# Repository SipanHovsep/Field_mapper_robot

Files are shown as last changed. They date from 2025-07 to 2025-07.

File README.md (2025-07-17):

# Field Mapper Robot

## Overview
Design of a **modular, cost‑effective robot** for mapping magnetic fields within a defined volume.
<div align="center">
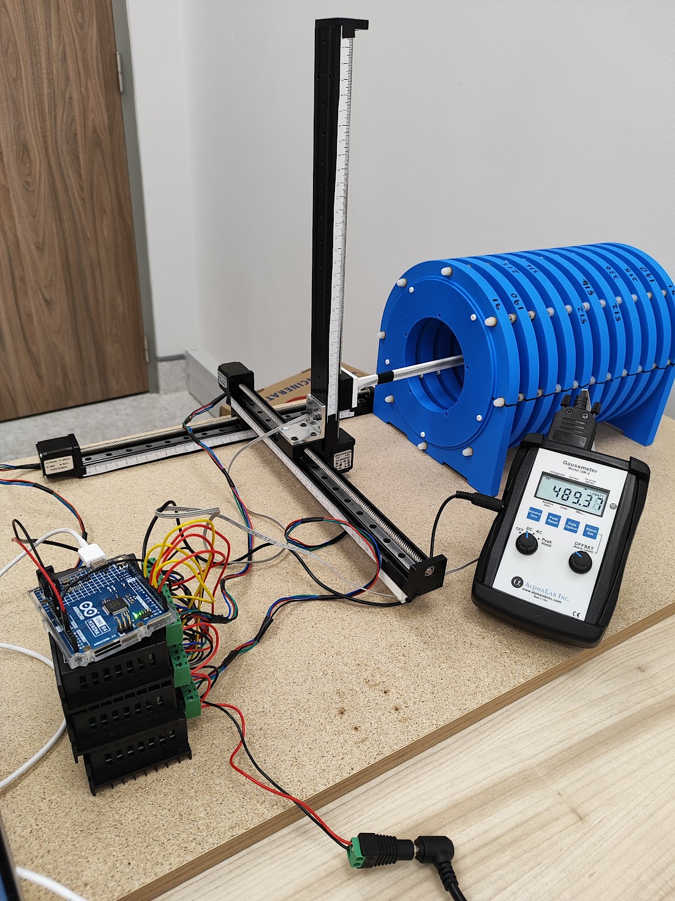
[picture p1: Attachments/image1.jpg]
  
</div>

## Software requirements
* **PyCharm** – Python IDE (Python 3.13) – [Link](https://www.jetbrains.com/pycharm/)
* **Arduino IDE** – Native Arduino software – [Link](https://www.arduino.cc/en/software/)

## Hardware requirements
* **CPU:** 64‑bit dual‑core (modern)  
* **RAM:** ≥ 8 GB (PyCharm needs 2 GB free)  
* **Storage:** ≥ 5 GB free SSD (PyCharm ≈ 3.5 GB + projects)  
* **OS:** Windows 10 64‑bit +, macOS 10.15 +, Ubuntu 20.04 +  
* Basic jumper wires for Arduino  
* M3 screws with nuts  
* USB‑C ↔ USB‑C / USB‑A ↔ USB‑C cable (Arduino Uno R4)  
* Wire cutter/stripper  
* Precision screwdriver set  

---

## Bill of Materials
| Component | Qty | Unit Price (USD) | Link |
|---|:---:|:---:|---|
| Linear stages (Z 300 mm, XY 300 mm – 12 mm pitch) | 1 | 338.54 | [Product](https://www.aliexpress.us/item/3256805348651313.html?spm=a2g0o.order_detail.order_detail_item.3.5fa4f19cjVbIP4&gatewayAdapt=glo2usa) |
| TB6600 stepper driver | 3 | 5.60 | [Product](https://www.aliexpress.us/item/3256805781393725.html?spm=a2g0o.order_detail.order_detail_item.2.1ed6f19cobQnNT&gatewayAdapt=glo2usa) |
| Arduino UNO R4 Minima | 1 | 16.00 | [Product](https://thepihut.com/products/arduino-uno-r4-minima) |
| Gaussmeter GM2 | 1 | 902.00 | [Product](https://www.alphalabinc.com/products/gm2/?srsltid=AfmBOor0p2l-VF9fIRODsZqY854WaDDNnBIFsOJ6kHjN2p6iCgCOzTLX) |
| **Total** |  | **1262.14** |  |

---

## High‑Level Workflow

<div align="center">
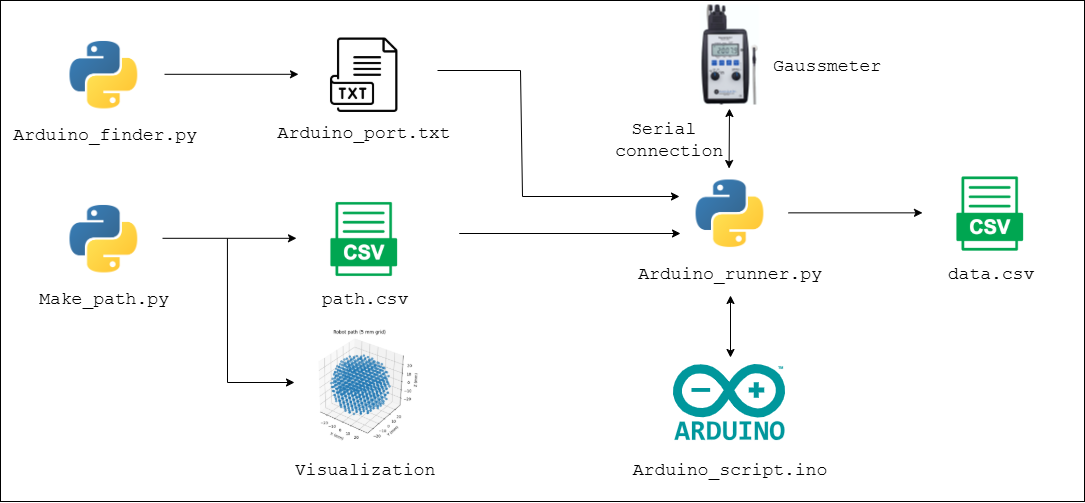
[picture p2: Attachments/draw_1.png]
System flowchart 1
  
</div>
<h3 align="center"><em>Software workflow diagram</em></h3>

<div align="center">
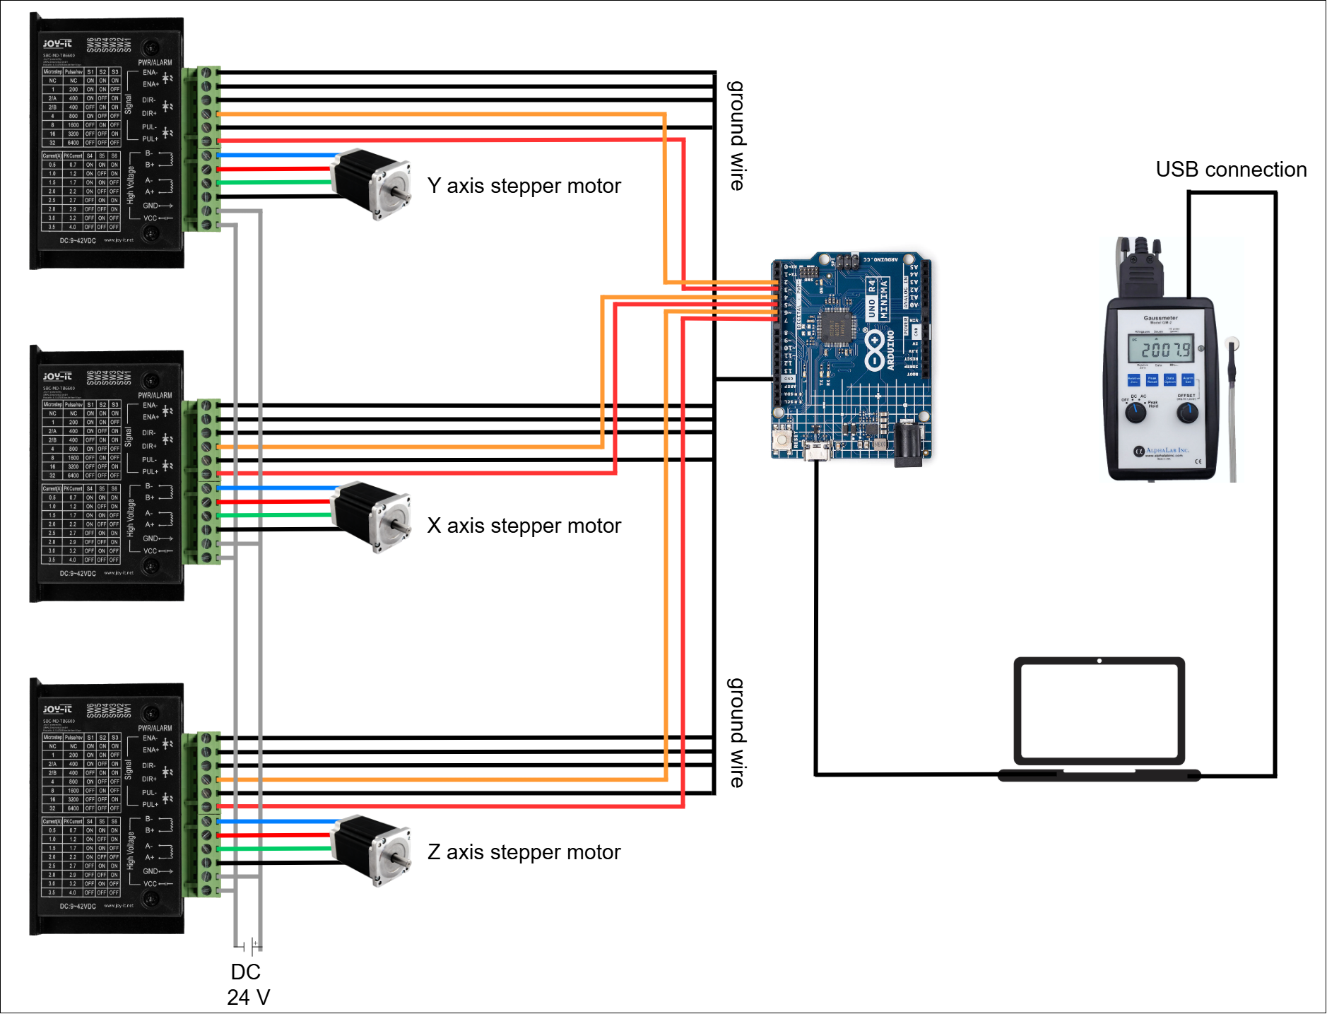
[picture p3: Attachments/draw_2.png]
System flowchart 2
  
</div>
<h3 align="center"><em>Wiring diagram</em></h3>

## Installation and Setup  

1. Clone the repository:  
    ```bash  
    git clone https://github.com/SipanHovsep/Field_mapper_robot
    ```  
2. Install dependencies:  
    ```bash  
    pip install -r requirements.txt  
    ```  
3. Connect the hardware as described in the wiring diagram.
4. Print the files in [3D print files](3D_print_files)
5. Connect and upload [`Arduino_script.ino`](scripts/Arduino_script.ino) to Arduino
6. Run [`Arduino_finder.py`](scripts/Arduino_finder.py)
7. Run [`Path_maker.py`](scripts/Path_maker.py)
8. Run [`Arduino_runner.py`](scripts/Arduino_runner.py)
9. Check out [`Supporting images`](Attachments/Supporting%20images/) for further images
---

## Scripts Overview  

### [`Arduino_finder.py`](scripts/Arduino_finder.py)

- Run once the arduino is connected 
- Finds the connection port name and writes it in Arduino_port.txt file 

### [`Path_maker.py`](scripts/Path_maker.py)

- Generates the path trajectory with discrete points
- Allows user to modify the trajectory and spacing between individual points
- Visualizes the path in 3D with exact sequence the robot would follow, for user to validate
- Writes the x y z coordinates of the path in the right order in "path.CSV" file

### [`Arduino_runner.py`](scripts/Arduino_runner.py)
  
- Allows user to input delay time for sensor read at each desired point and control the speed of robot movement
- Retrieves the coordinates from "path.CSV" file
- Generates text commands to move the robot according to the path
- Sends text commands to arduino at 9600 baud (defined by user) via Arduino port retrieved from Arduino.txt file
- Establishes a serial connection with Gaussmeter through usb port
- Records voltage readings of Gaussmeter per data point and appends to corresponding coordinate
- Generates Data.CSV, containing x y z reading values for each coordinates

### [`Arduino_script.ino`](scripts/Arduino_script.ino)
- Defines Pin map of the arduino
- Listens for simple text commands (X+, X-, Y+, Y-, Z+, Z-,) sent over USB at 9600 baud (Links [`Arduino_runner.py`](scripts/Arduino_runner.py) with Arduino)
- Moves the robot 1 mm per command by pulsing the chosen step pin 533.34 times (defined by callibration)

---
## Assembly Tips

### 1 · Axis Ruler for Quick Calibration
<div align="center">
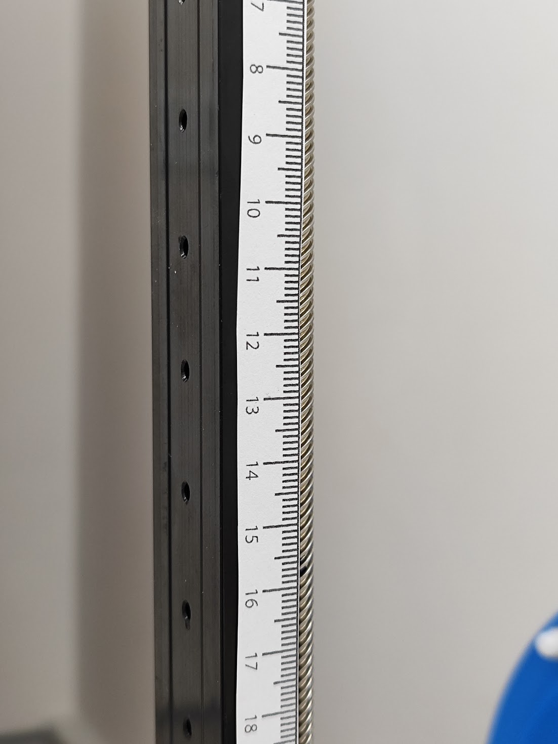
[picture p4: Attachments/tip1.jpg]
  
</div>
Attaching a printed ruler minimises calibration time and ensures precise step‑to‑millimetre mapping.

### 2 · Mount on a Rigid Base
<div align="center">
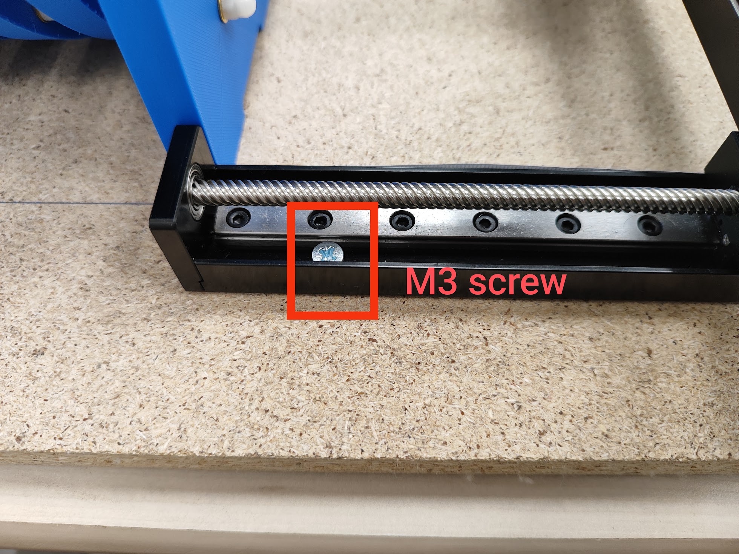
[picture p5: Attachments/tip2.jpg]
Robot mounted on wooden panel
  
</div>
Secure the frame to a **≥ 40 × 60 × 1.5 cm** wooden panel for stability during operation.

### 3 · Variable DC Power Supply
<div align="center">
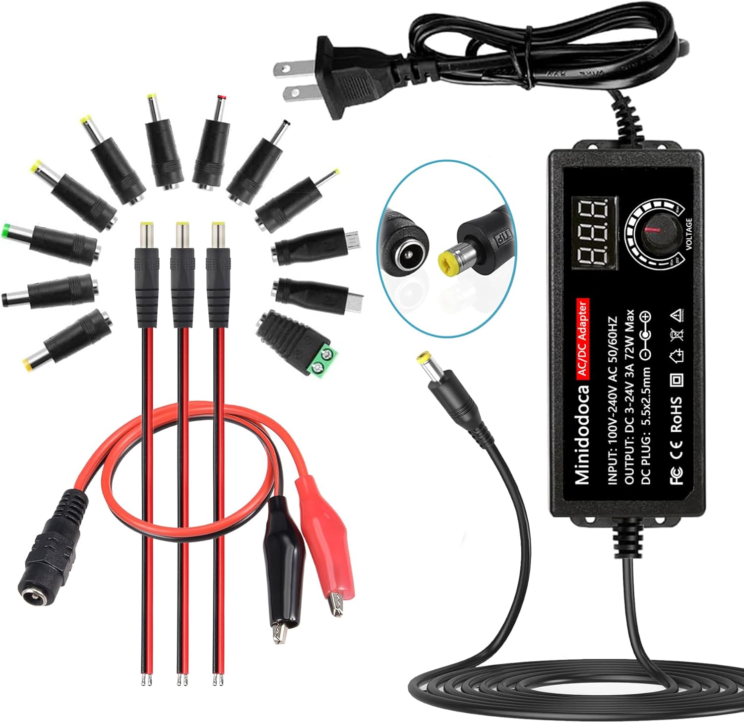
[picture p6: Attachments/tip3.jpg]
Variable DC power supply
  
</div>
A low‑cost variable supply (~15 USD) simplifies testing different motor voltages and current limits.

### 4 · TB6600 DIP‑Switch Settings
<div align="center">
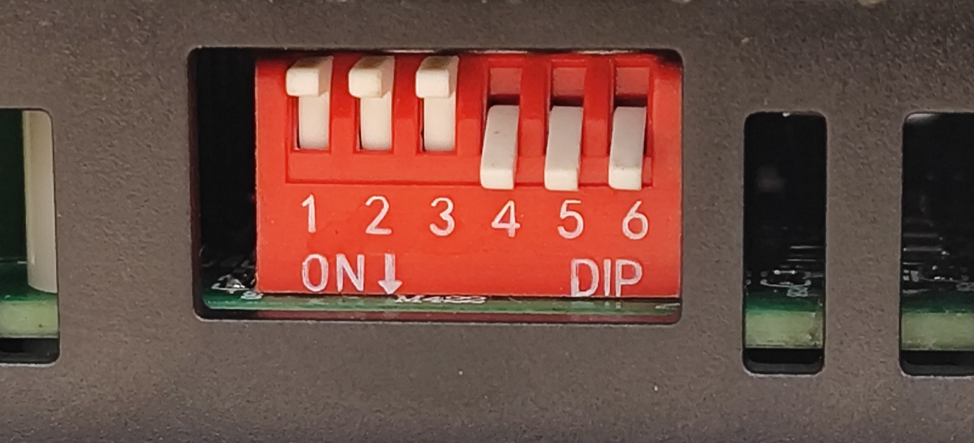
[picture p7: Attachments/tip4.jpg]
TB6600 switch positions
  
</div>
Set switches **S1–S6 = OFF** to match the firmware micro‑stepping and protect the motors.

---

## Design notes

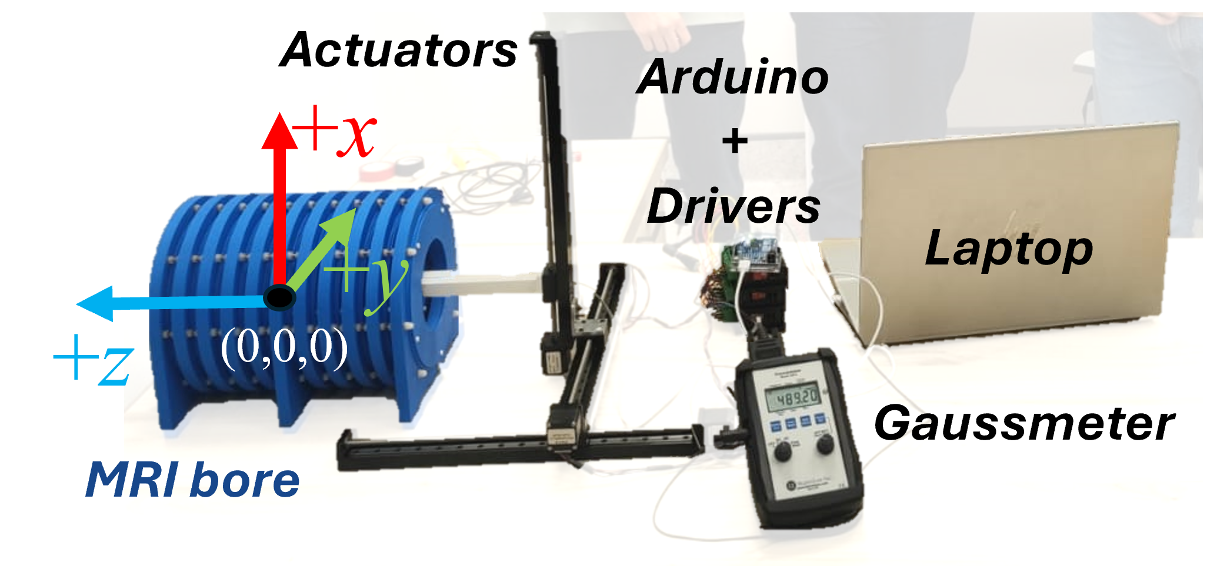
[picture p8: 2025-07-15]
Attachments/Images/Mapper2.png

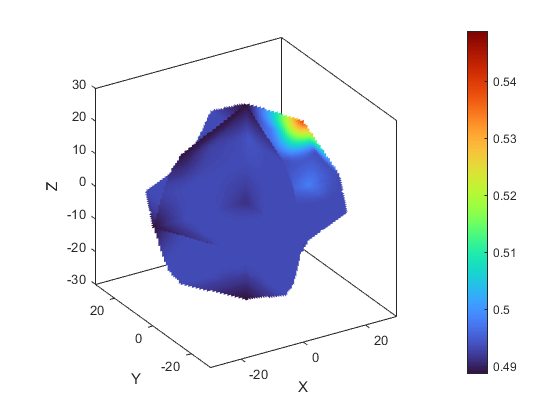
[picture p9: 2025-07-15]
Attachments/Images/MAP_118.png

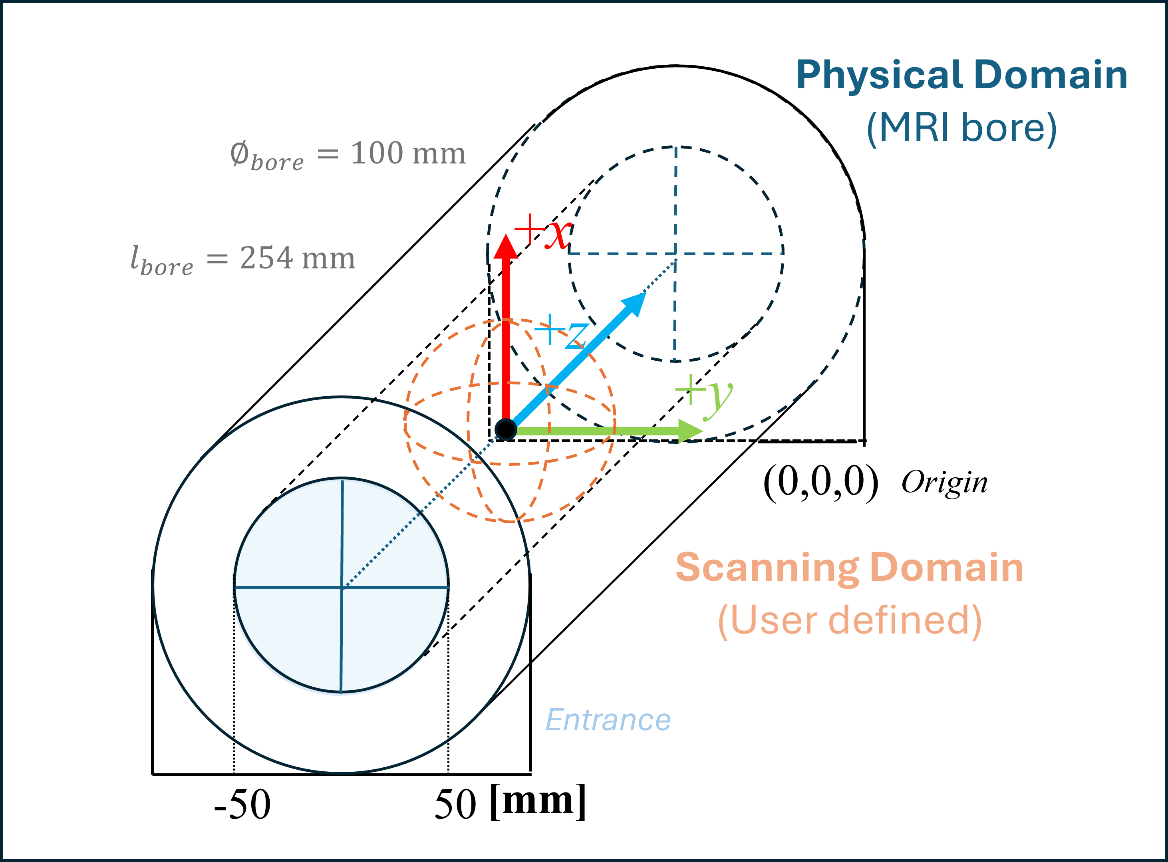
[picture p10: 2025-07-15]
Attachments/Images/scheme3.png

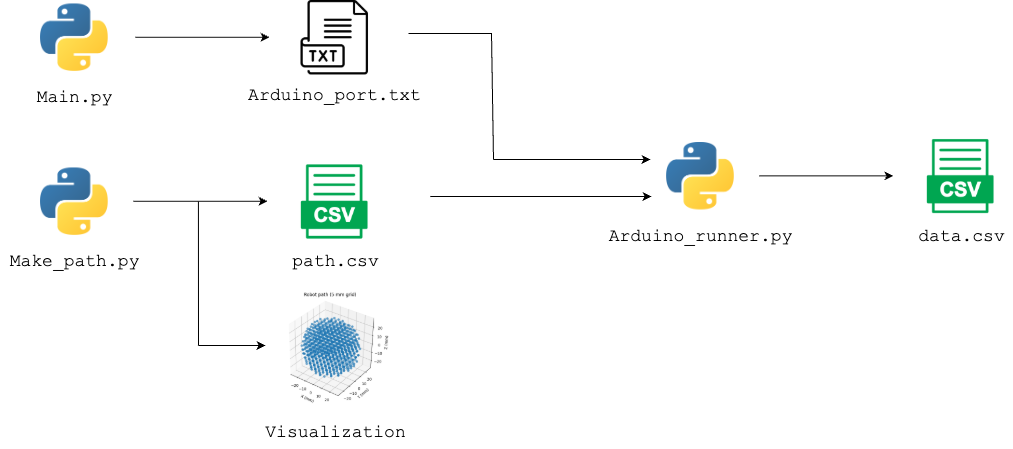
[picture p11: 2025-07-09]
Attachments/Field_mapper_robot.drawio.png

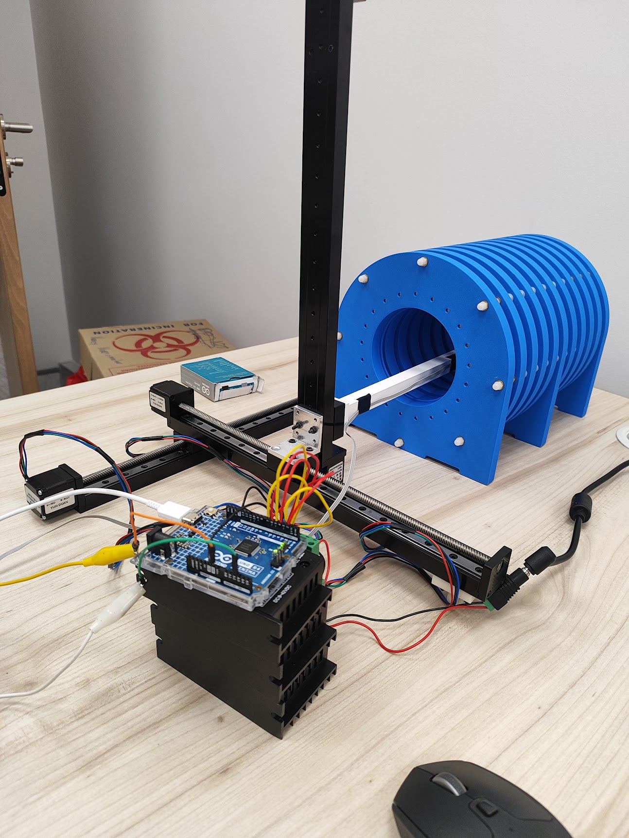
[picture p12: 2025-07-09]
Attachments/Robot.jpg

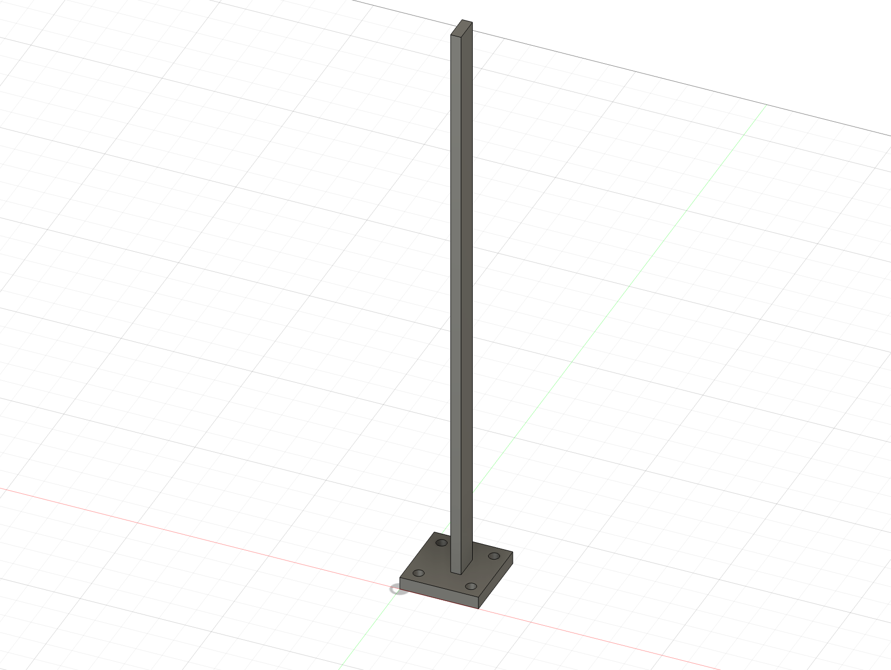
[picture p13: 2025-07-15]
Attachments/mount.png

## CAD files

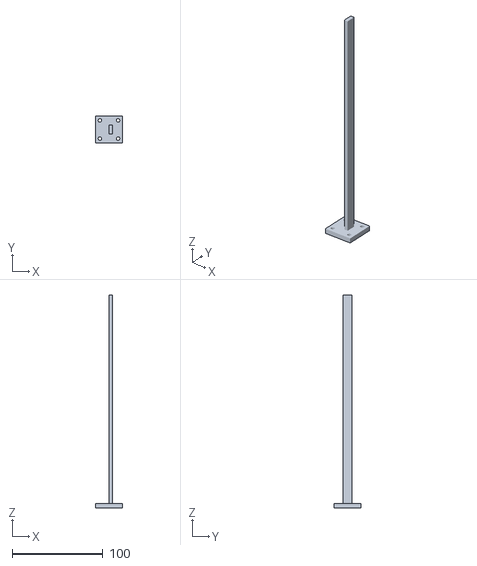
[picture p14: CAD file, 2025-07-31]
3D print files/Sensor_mount_1.stl
30.0 x 30.0 x 235.0

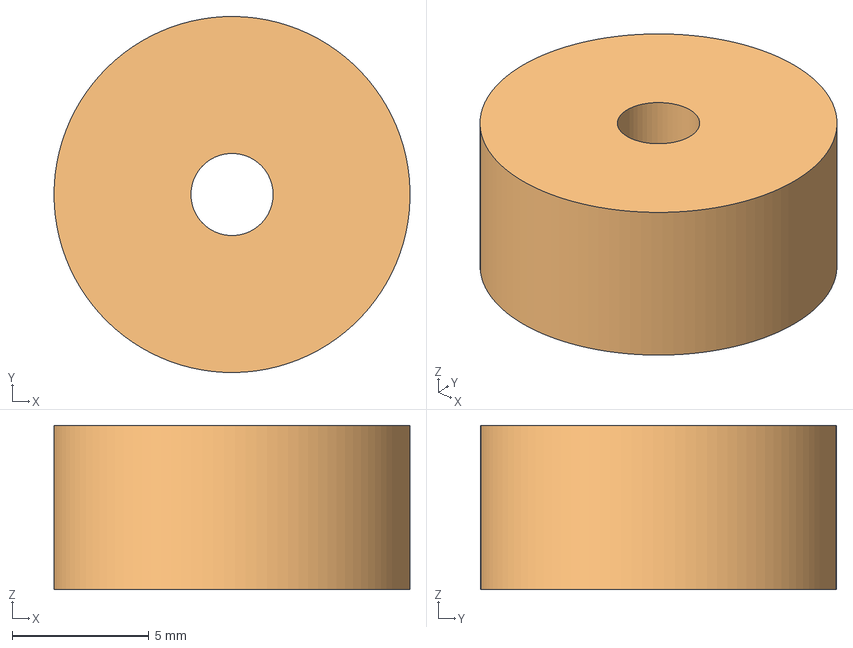
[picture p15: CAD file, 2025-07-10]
3D print files/wheel.3mf
13.0 x 13.0 x 6.00 mm

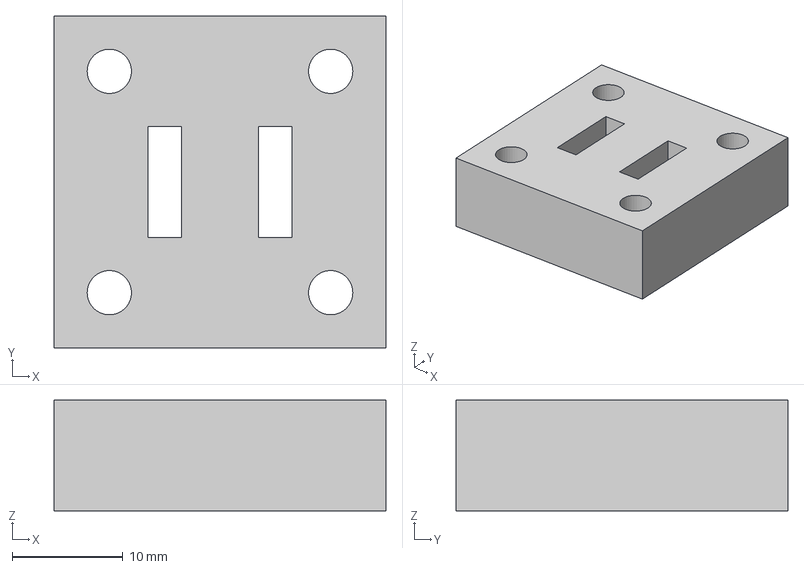
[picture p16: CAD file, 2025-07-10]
3D print files/base.3mf
30.0 x 30.0 x 10.0 mm

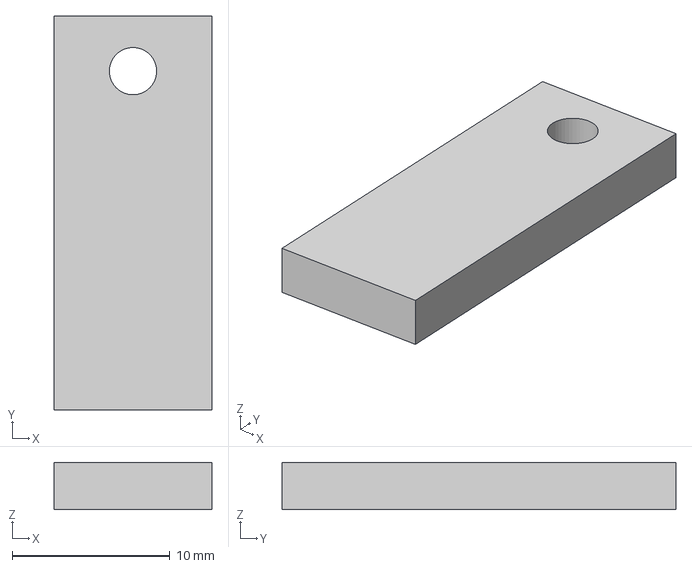
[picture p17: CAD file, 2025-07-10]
3D print files/stick.3mf
10.0 x 25.0 x 3.00 mm

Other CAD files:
3D print files/Sensor_mount_1.f3d

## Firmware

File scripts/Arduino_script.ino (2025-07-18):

/* ──────────── pin map (unchanged) ──────────── */
const int Step_z = 7, Dir_z = 6;
const int Step_x = 5, Dir_x = 4;
const int Step_y = 3, Dir_y = 2;

#define STEPS_PER_MM  533.33333334   // 1‑mm move = 533 pulses
#define PULSE_US      200            // HIGH / LOW time per pulse

void setup() {
  Serial.begin(9600);                // must match the Python BAUD
  pinMode(Step_z, OUTPUT);  pinMode(Dir_z, OUTPUT);
  pinMode(Step_x, OUTPUT);  pinMode(Dir_x, OUTPUT);
  pinMode(Step_y, OUTPUT);  pinMode(Dir_y, OUTPUT);
}

/* ───────── main loop: parse newline‑terminated commands ───── */
void loop() {
  static char line[16];
  static byte idx = 0;

  while (Serial.available()) {
    char c = Serial.read();

    if (c == '\n' || c == '\r') {     // end of command
      line[idx] = '\0';
      idx = 0;
      handleCmd(line);
    } else if (idx < sizeof(line) - 1) {
      line[idx++] = c;               // build token
    }
  }
}

/* ───────── command dispatcher ───────── */
void handleCmd(const char *cmd) {
  if      (!strcmp(cmd, "X+")) { digitalWrite(Dir_x, HIGH);  moveSteps(Step_x); }
  else if (!strcmp(cmd, "X-")) { digitalWrite(Dir_x, LOW);   moveSteps(Step_x); }
  else if (!strcmp(cmd, "Y+")) { digitalWrite(Dir_y, HIGH);  moveSteps(Step_y); }
  else if (!strcmp(cmd, "Y-")) { digitalWrite(Dir_y, LOW);   moveSteps(Step_y); }
  else if (!strcmp(cmd, "Z+")) { digitalWrite(Dir_z, HIGH);  moveSteps(Step_z); }
  else if (!strcmp(cmd, "Z-")) { digitalWrite(Dir_z, LOW);   moveSteps(Step_z); }
  /* any other string is ignored */
}

/* ───────── 1‑mm step routine ───────── */
void moveSteps(int stepPin) {
  for (int i = 0; i < STEPS_PER_MM; ++i) {
    digitalWrite(stepPin, HIGH);
    delayMicroseconds(PULSE_US);
    digitalWrite(stepPin, LOW);
    delayMicroseconds(PULSE_US);
  }
}

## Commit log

2025-07-09 Create Arduino
    Code for Arduino IDE
2025-07-09 Update Arduino
2025-07-10 Add 3d files
    [base.3mf, stick.3mf, wheel.3mf]
2025-07-11 Create calibration_test
2025-07-16 Create arduino_final
